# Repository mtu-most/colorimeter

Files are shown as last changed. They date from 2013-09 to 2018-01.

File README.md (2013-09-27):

#Colorimeter and nephalometer firmware

With the files in this directory, you can create a colorimeter and/or
nephalometer, if you have the tools.  You find here:

- colorimeter.ino: c++ source for the firmware, to be uploaded to the arduino.
- \*.scad: models for all the parts which should be produced on a 3-D Printer.  Use OpenSCAD to turn them into STLs.
- colorimeter.sch: Schemetic of the electronics.  Use KiCad to open it.  You are expected to solder everything by hand, so there is no board layout.

To compile the firmware, you need the LcdMenu and DuplexFrequencyCounter libraries from our
[other repository](https://github.com/mtu-most/arduino-libraries).

## Required components
Arduino fio
Adafruit lcd shield PCB
3.3 V lcd unit
3 small PCBs
2 LEDs (860 nm for nephalometry and 620 nm for colorimetry)
3 light to frequency encoders
Some wire to connect it all
Some filament to print the casing
Battery
Some nuts and bolts

## Required tools
3-D printer
FTDI (or equivalent) 3.3 V serial communication cable
Soldering iron

## Steps
1. Load the firmware in the Arduino IDE to flash it into the Arduino (or use make upload).
1. Print all the parts
1. Solder the lcd unit to the lcd shield
1. Cut 3 PCBs to size for the slots
1. Solder the components to the PCBs according to the schematic.  Don't solder anything to the ardiuno; use connectors instead.  Each LED goes on a board with a sensor watching it, the third sensor goes on a board of its own, looking away from the board.
1. Put it all together and close it with screws.

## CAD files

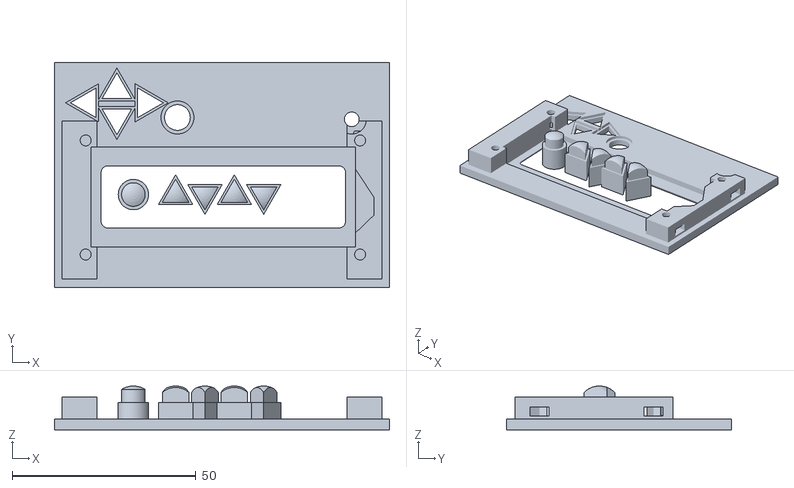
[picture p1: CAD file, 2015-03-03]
stl/adafruit_lcd_shield_face.stl
91.3 x 61.3 x 12.0

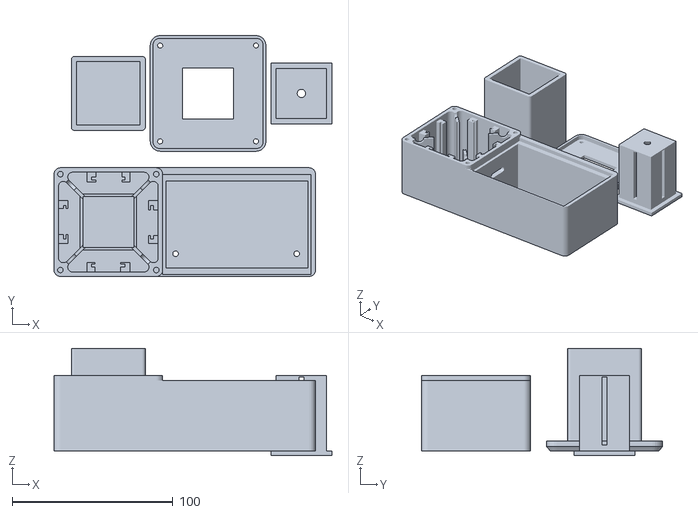
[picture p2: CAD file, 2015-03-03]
stl/Colorimeter_v02.stl
172.8 x 149.8 x 66.6

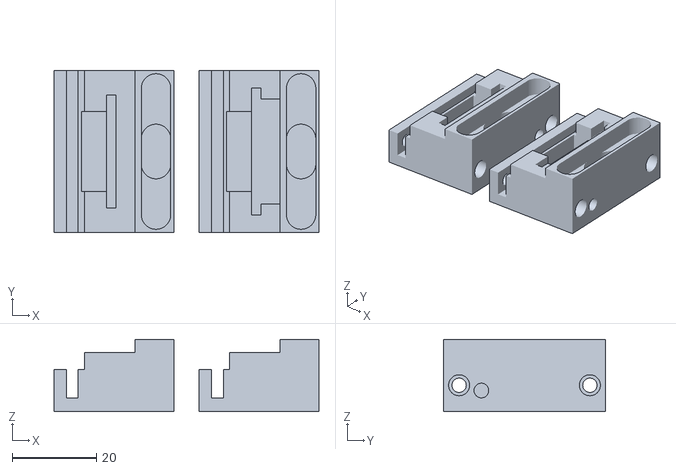
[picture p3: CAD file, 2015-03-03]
stl/board_clips.stl
63.0 x 38.5 x 17.1

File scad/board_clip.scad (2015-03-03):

/**********

 Clips sandwich the various boards together using the holes in the LCD shield and LCD board to
 hold the package together.

 The entire assembled unit will fit inside the colorimeter case and will be held in place by a pair of
 M3 screws through the bottom of the case.

**********/

include <adafruit_lcd_shield_face.scad>
include <fio.scad>
include <fasteners.scad>

// in order to be consistent with fio and adafruit libraries, the clip origin will be the lower left
// as if the LCD shield were sitting atop the clip in it's design orientation

// l || x
// w || y
// t || z

xbee = 0;

// some more fio dims
t_fio_overall = (xbee == 1) ? 16 : 12;  // thickness of Fio with xbee onboard
t_fio_bd_to_xbee = (xbee == 1) ? 8.5 : 4.5; // thickness of fio and xbee w/o battery connector thickness
w_fio_xbee = 25; // width of the xbee socketed
w_fio_sockets = 19; // combined width of battery and USB sockets
clear_w_fio = 1.5;  // additional clearance for fio board
clear_t_fio = 0.75;

t_bd714_overall = 16; // thickness of the populated Adafruit LCD shield
t_lcd_overall = 11.5; // overall thickness of only the LCD board
clear_t_bd714 = 0.75;

l_battery = 63;
w_battery = 37;
t_battery = 7;

clear_comp = 1.5; // clearance between components
clear_lcd = 3; // clearance between lcd and shield

d_holes = 3.4;

// the adafruit LCD board is the longest and widest
l_overall = l_bd714 + 6; // add 3mm to each end
w_overall = w_bd714; // width same as the width of the LCD shield board

// clip dimensions
l_clip = (l_overall - l_battery) / 2 + 5; // battery is shortest - give it 5mm recess
w_clip = w_battery + clear_comp; // battery is the widest component
t_clip = clear_lcd + clear_comp * 2.5 + t_battery + t_fio_overall + t_bd714 + clear_t_bd714;

t_overall = t_clip + t_lcd_overall + lcd_relief;

echo(str("t_clip: ", t_clip, " t_overall: ", t_overall));

// x offsets relative to overall width of assembly; l_overall
x_offset_battery = (l_overall - l_battery) / 2;
x_offset_fio = (l_overall - l_fio) / 2;
x_offset_bd714 = (l_overall - l_bd714) / 2;
x_offset_holes_bd714 = (l_overall - ccl_holes_bd714) / 2;
x_offset_case_screw = x_offset_bd714 + 2;

// y offsets are relative to w_clip
y_offset_battery = t_battery/2 + (w_clip - w_battery) / 2;
y_offset_fio = (w_clip - w_large_fio - clear_w_fio) / 2;
y_offset_bd714 = -1; // there is no y offset for the LCD shield as it's the widest
y_offset_case_screw = 9;

z_offset_battery = (clear_comp + t_battery)/2; // on the bottom
z_offset_fio = clear_comp * 1.5 + t_battery + t_fio_bd_to_xbee; // in middle
z_offset_bd714 = clear_comp * 2.5 + t_battery + t_fio_overall;

module clip(fio_wide_end = 1) {
	difference() {
		// the body of the clip
		cube ([l_clip, w_clip, t_clip]);
		
		// battery opening - bottom most
		translate([x_offset_battery, y_offset_battery, z_offset_battery])
			rotate([0, 90, 0])
				battery();

		if (fio_wide_end == 1) {
			// fio above battery - one end is wider than the other this is wide end w/ sockets
			translate([x_offset_fio, y_offset_fio, z_offset_fio]) {
				cube([l_fio, w_large_fio + clear_w_fio, t_fio + clear_t_fio]); // fio board
		
				translate([0, (w_large_fio + clear_w_fio - w_fio_xbee)/2,  - t_fio_bd_to_xbee])
					cube([l_fio, w_fio_xbee, t_fio_bd_to_xbee]); // xbee opening
		
				translate([-x_offset_fio - 1, (w_large_fio + clear_w_fio - w_fio_sockets)/2, clear_t_fio + t_fio])
					cube([l_fio, w_fio_sockets, 6]); // fio socket opening
			}
	
			// nut trap and hole for attaching to case
			translate([x_offset_case_screw, y_offset_case_screw, 2]) 
				nut_trap();

			// the contrast pot on the shield gets in the way of the one corner:
//			translate([(l_overall - l_bd714) / 2, w_clip-1, t_clip - 5])
//				cube([8, 5, 10]);
		}
		else {
			translate([x_offset_fio, y_offset_fio + (w_large_fio - w_small_fio) / 2, z_offset_fio]) {
				cube([l_fio, w_small_fio + clear_w_fio, t_fio + clear_t_fio]); // fio board

				translate([-x_offset_fio - 1, (w_small_fio + clear_w_fio - w_fio_sockets)/2, clear_t_fio + t_fio])
					cube([l_fio, w_fio_sockets, 6]); // wire recess
			}

			// nut trap and hole for attaching to case
			translate([x_offset_case_screw, w_clip - y_offset_case_screw, 2]) 
				nut_trap();
		}

		// chop some relief for the fio
		translate([x_offset_fio + 3, -1, 1.5 * clear_comp + t_battery])
			cube([l_clip, w_clip + 2, t_clip]);

		// LCD shield board
		translate([x_offset_bd714, y_offset_bd714, z_offset_bd714])
			cube([l_bd714, w_bd714, t_bd714 + clear_t_bd714]);
	
		// clearance is required for sockets and joints on LCD board
		translate([x_offset_bd714 + 7, -1, z_offset_bd714 - clear_comp])
			cube([l_clip, w_clip + 2, 20]);
	
		// holes for screws to affix boards together
		translate([x_offset_holes_bd714, (w_clip - ccw_holes_bd714)/2, -1])
			holes(d_holes, t_clip+2);
	
		// holes for screw caps
		translate([x_offset_holes_bd714, (w_clip - ccw_holes_bd714)/2, -1])
			holes(5, t_clip - 16 + (t_standoff_lcd - h_M25_nut)/2 + t_bd_lcd + 1);	
	
		// recess for cables
		translate([-1, (w_large_fio + clear_w_fio - w_fio_sockets)/2 + y_offset_fio, 5])
			cube([4, w_fio_sockets, w_fio_sockets]);
	}

	// need something to tell the slicer there's a bridge:
		translate([3, 0, 0])
			cube([0.25, w_clip, t_clip]);

}

module battery() {
	hull() {
		cylinder (r=t_battery/2, h=l_battery);

		translate([0, w_battery-t_battery, 0])
			cylinder (r=t_battery / 2, h=l_battery);
	}

	// hole for cables
	translate([0, (w_battery - t_battery) / 2 - 3, -20])
		hull() {
			cylinder (r=t_battery/2, h=l_battery + 40);
	
			translate([0, 6, 0])
				cylinder (r=t_battery / 2, h=l_battery + 40);
		}
}

module holes(diameter, height, fn=48) {
	cylinder(r=diameter/2, h=height, $fn=fn);

	translate([0, ccw_holes_bd714, 0])
		cylinder(r=diameter/2, h=height, $fn=fn);
}

module nut_trap() {
	hull() {
		cylinder(r=d_M3_nut/2, h=h_M3_nut, $fn=6);

		translate([-15, 0, 0])
			cylinder(r=d_M3_nut/2, h=h_M3_nut, $fn=6);
	}

	translate([0, 0, -5])
		cylinder(r=d_M3_screw/2, h=15);
}

module both_clips() {
	rotate([0, 270, 0])
		clip(fio_wide_end = 0);
	
	translate([t_clip+6, 0, 0])
		rotate([0, 270, 0])
			clip(fio_wide_end = 1);
}

// the case interior
module case_interior() {
	// some clearance must be built in
	clear_faceplate = 1;
	clear_interior = 1;
	x_offset_int = (l_face + clear_faceplate - (l_overall + clear_interior)) / 2;
	y_offset_int = (w_face + clear_faceplate - (w_overall + clear_interior)) / 2;
	union() {
		translate([x_offset_int, y_offset_int, 0]) {
			cube([l_overall + clear_interior, w_overall + clear_interior, t_overall + clear_interior]);

		translate([x_offset_case_screw + clear_interior, y_offset_case_screw, -20])
			cylinder(r=d_M3_screw / 2, h = 21);

		translate([l_overall - clear_interior - x_offset_case_screw, y_offset_case_screw, -20])
			cylinder(r=d_M3_screw / 2, h = 21);
		}
		// the faceplate is inset
		translate([0, 0, t_overall - face_thickness + clear_interior])
			cube([l_face + clear_faceplate, w_face + clear_faceplate, face_thickness + 1]); // add 1mm so it clears the top

	}
}

module female_sizeM() {
	union() {
		cylinder(r=4, h=8);

		cylinder(r=5.25, h=2.5);

		translate([0, 0, 5])
			cylinder(r=5.75, h=4, $fn=6);
	}
}

module test_case() {
	difference() {
		translate([2, 2, 0])
		hull() {
			for (i=[0:1]) {
				for (j=[0:1]) {
					translate([i*(l_face + 1), j*(w_face + 1), 0])
						cylinder(r=2, h=t_overall);
				}
			}
		}
	
		translate([2, 2, 2])
			case_interior();

		// power connector
		translate([25, w_overall + 3, 10])
			rotate([270, 0, 0])
				female_sizeM();

		// opening for a cable
		translate([l_overall + 3, w_overall - 17, 4])
			rotate([0, 90, 0])
			rotate([0, 0, 90])
				hull() {
					cylinder(r=0.75, h=5);

					translate([14, 0, 0])
						cylinder(r=0.75, h=5);
			}
	}
}

//test_case();

//both_clips();

//clip(fio_wide_end = 1);

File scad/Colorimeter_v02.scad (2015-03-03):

/**********

This is for the portable version - it shouldn't be played with too much as everything fits with this config!!!

**********/

include <board_clip.scad>

// customizable parameters

// distance from center of cuvette to detector or LED
signal_half_path = 28; // [45:60]

// This sets the number of straight signal paths; 2 paths will generate a square, 3 a hexagon, 4 an octagon...
signal_paths = 2; // [2:4]

// Width of boards sensors and sources are mounted on (mm)
board_width = 20; // [20:30]

// Thickness of boards (mm)
board_thickness = 1.8;

// Board standoff (mm)
board_standoff = 3; // [3:5]

// Cuvette diameter (mm)
cuvette_diameter = 17;

// 1=hemispherical bottom; 0=flat bottom
hemispherical_bottom = 1; // [0:1] 

// Overall length of the cuvette (mm)
cuvette_length = 102; // [30:100]

// Amount of cuvette in analysis area (mm)
analysis_depth = 44.2; // [20:55]

render(5);

module render(render_part) {

	if (render_part == 1)
		case();

	if (render_part == 2)
		rotate([0, 0, 45])
			lid();

	if (render_part == 3)
		translate([0, 0, analysis_depth+t_wall_ext*2])
			mirror([0, 0, 1])
				holder();

	if (render_part == 4)
		cover();

	if (render_part == 5)
		translate([0, 80, 0])
			rotate([0, 0, 45])
				cover();

		case();

		translate([62, 80, 0])
			rotate([0, 0, 45])
				lid();

		translate([120, 80, 0])
			holder();
}

// ignore variable values

// clearances, wall thicknesses, etc.
pad_board = 3;
clear_board = 0.4;
clear_cuvette = 0.4;
clear_faceplate = 4;
t_wall_ext = 2.8; // exterior wall thickness
t_wall_int = 2.1; // interior wall thickness
r_apex_ext = 4; // radius of exterior corners
r_apex_int = 3; // radius of interior corners
overlap_lid = 3.5;
flange_holder = 5;

// segment dimensions representing exterior of case
// everything is calculated in terms of circular segments from which trapezoids are constructed
a_seg = 360/signal_paths/2; // angle of segment arc
tan_h_a_seg = tan(a_seg/2);
cos_h_a_seg = cos(a_seg/2);
sin_h_a_seg = sin(a_seg/2);
h_ext = signal_half_path+t_wall_ext+board_standoff; // height of the triangle making up the segment
r_ext = h_ext/cos_h_a_seg; // radius of the segment; distance from center to corner
t_ext = analysis_depth+t_wall_ext; // thickness of the segment

echo(str("2*h_ext = ", 2 * h_ext));
echo(str("t_ext =", t_ext));

// cuvette holder dimensions -- like the case, it is based on a segment
h_holder = 25.4/2+2.8; // this is the height of triangle making up the holder, must be big enough for the largest cuvette and have allowance for wall thickness
r_holder = h_holder/cos_h_a_seg;
clear_holder = 0.5;

// radii of rounded apex centers
r_c_apex_ext = r_ext-r_apex_ext/cos_h_a_seg;
r1_c_apex_int = r_ext-(r_apex_int+t_wall_ext)/cos_h_a_seg;
r2_c_apex_int = r_holder+r_apex_int/cos_h_a_seg;

// cavities are trapezoids with rounded apexes:
b1 = r1_c_apex_int*sin_h_a_seg*2-(2*r_apex_int+t_wall_int)/cos_h_a_seg;
b2 = r2_c_apex_int*sin_h_a_seg*2-(2*r_apex_int+t_wall_int)/cos_h_a_seg;
h = (r1_c_apex_int-r2_c_apex_int)*cos_h_a_seg;

d_M3_screw = 3.5; // measured 2.9
d_M3_screw_head = 5.8; // measured 5.5
d_M3_washer = 6.9; // measured 6.7
d_M3_nut = 6.2;
h_M3_nut = 2.7; // measured 2.35
d_M3_cap = 5.5;
h_M3_cap = 3;

d_M4_screw = 4.3;
d_M4_cap = 7.4; // measured 12
h_M4_cap = 4;
d_M4_nut = 8.7;
h_M4_nut = 3.5; // measured 3.1
h_M4_locknut = 5;
d_M4_washer = 9; // measured 8.75
h_M4_washer = 0.75;

d_M6_screw = 6.5;
d_M6_nut = 11.3;
h_M6_nut = 4.2;

d_M8_screw = 8.4;
d_M8_nut = 15;
h_M8_nut = 6.35;
d_M8_washer= 16;
h_M8_washer = 1.5;

module exterior_sensor(height) {
	union() {
		hull() {
			for (i=[0:signal_paths*2-1]) 
				rotate([0, 0, a_seg*i])
					translate([0, r_c_apex_ext, 0])
						cylinder(r=r_apex_ext, h=height, $fn=24);
		}

	}
}

module exterior_interface(height) {
	hull() {
		translate([-h_ext+r_apex_ext, -l_face/2-r_apex_ext, 0])
			cylinder(r=r_apex_ext, h=height, $fn=24);

		translate([h_ext-r_apex_ext, -l_face/2-r_apex_ext, 0])
			cylinder(r=r_apex_ext, h=height, $fn=24);

		translate([h_ext-r_apex_ext, l_face/2+r_apex_ext, 0])
			cylinder(r=r_apex_ext, h=height, $fn=24);

		translate([-h_ext+r_apex_ext, l_face/2+r_apex_ext, 0])
			cylinder(r=r_apex_ext, h=height, $fn=24);
	}
}

module cavity() {
	x_retainer = board_width+2*(clear_board+pad_board);
	y_retainer = 2*board_standoff;

	translate([0, -h/2-r_apex_int, 0])
	difference() {
		union() {
			// trapezoid with rounded apexes:
			hull() {
				translate([-b1/2, -h/2, 0])
					cylinder(r=r_apex_int, h=t_ext);
		
				translate([b1/2, -h/2, 0])
					cylinder(r=r_apex_int, h=t_ext);
		
				translate([b2/2, h/2, 0])
					cylinder(r=r_apex_int, h=t_ext);
		
				translate([-b2/2, h/2, 0])
					cylinder(r=r_apex_int, h=t_ext);
			}
	
			// wire race
			translate([-b1/2+r_apex_int*sin_h_a_seg, -h/2+r_apex_int*cos_h_a_seg, t_ext-t_wall_ext])
				rotate([0, -90, -a_seg/2])
					cylinder(r=3.5, h=t_wall_int+r_apex_int+1);
		}
	
		// sensor/LED board retainers
		translate([-x_retainer/2, -h/2-r_apex_int, -1])
			difference() {
				cube([x_retainer, y_retainer, t_ext-4]);

				translate([pad_board, board_standoff, -1])
					cube([x_retainer-2*pad_board, board_thickness, t_ext-2]);

				translate([pad_board+2, 0, -1])
					cube([board_width-4, y_retainer+1, t_ext-2]);
			}

		// lip at bottom of cuvette holder
		translate([-b2*2, h/2+1, -1])
			cube([b2*4, 3, 2.5]);

	}
}

module case(
	portable = 1) {

	difference() {
		union() {
			rotate([0, 0, a_seg/2])
				exterior_sensor(t_ext);

			if (portable == 1)
				hull() {
					translate([h_ext + 91, h_ext - r_apex_ext, 0])
						cylinder(r=r_apex_ext, h=t_ext-3, $fn=24);
	
					translate([h_ext + 91, -h_ext + r_apex_ext, 0])
						cylinder(r=r_apex_ext, h=t_ext-3, $fn=24);

					translate([h_ext - r_apex_ext, h_ext - r_apex_ext, 0])
						cylinder(r=r_apex_ext, h=t_ext-3, $fn=24);
	
					translate([h_ext - r_apex_ext, -h_ext + r_apex_ext, 0])
						cylinder(r=r_apex_ext, h=t_ext-3, $fn=24);
				}
		}

		// cavities
		for (i=[0:signal_paths*2-1])
			rotate([0, 0, a_seg*i])
				translate([0, -h_holder, t_wall_ext])
					cavity();

		rotate([0, 0, a_seg/2]) {
			translate([0, 0, t_ext-16+t_wall_ext])
				holes(d_M3_screw/2, 16-t_wall_ext+1, 24);
	
			translate([0, 0, -1])
				holes((d_M3_nut+1)/2, t_ext-16+t_wall_ext-0.25+1, 6);
		}
	
		// cuvette holder
		translate([0, 0, t_wall_ext])
			rotate([0, 0, (1-signal_paths%2)*a_seg/2])
				cylinder(r=r_holder+clear_holder, h=t_ext, $fn=signal_paths*2);

		if (portable == 1) {
			// interior of electronics case
			translate([h_ext, -(w_face + clear_faceplate)/2, 2])
				case_interior();

			// power connector
			translate([h_ext + (l_overall + 2 * t_wall_ext)/2 - 10, h_ext - r_apex_ext - 2.5, 10])
				rotate([270, 0, 0])
					rotate([0, 0, 30])
						female_sizeM();

			// switch
//			translate([h_ext + (l_overall + 2 * t_wall_ext)/2 + 10,  h_ext - r_apex_ext - 0.5, 10])
//				rotate([270, 0, 0])
//					switch();
		}

		// wire entry
		rotate([0, 0, -90])
		translate([0, h_ext-t_wall_ext-1, t_ext - 20])
			rotate([-90, 0, 0])
				hull() {
					translate([-board_width/2 + 4, 0, 0])
						cylinder(r=2, h=t_wall_ext+5);

					translate([board_width/2 - 4, 0, 0])
						cylinder(r=2, h=t_wall_ext+5);
				}
	}

/*
	// following to check wall thicknesses are correct
	translate([0, h_ext-t_wall_ext/2, 0])
		#cylinder(r=t_wall_ext/2, h=100, $fn=48);
	
	rotate([0, 0, a_seg/2])
	translate([0, r_holder, 0])
		#cylinder(r=t_wall_int/2, h=100, $fn=48);
*/
}

module holes(radius, height, fn) {
	for (i=[0:signal_paths*2-1]) {
		rotate([0, 0, a_seg*i])
			translate([0, -r_c_apex_ext, 0])
				cylinder(r=radius, h=height, $fn=fn);
	}
}

module holder() {
	rotate([0, 0, a_seg/2])
		difference() {
			union() {
				// body
				cylinder(r=r_holder+clear_cuvette/2, h=analysis_depth+t_wall_ext, $fn=signal_paths*2);
	
				// flange
				translate([0, 0, analysis_depth+t_wall_ext])
					cylinder(r=r_holder+flange_holder, h=t_wall_ext, $fn=signal_paths*2);
			}

			if (hemispherical_bottom == 0) {
				cylinder(r=cuvette_diameter/2+clear_cuvette/2, h=analysis_depth+2*t_wall_ext+1);
			}
			else {
				translate([0, 0, cuvette_diameter/2])
					union() {
						sphere(r=cuvette_diameter/2+clear_cuvette);

						cylinder(r=cuvette_diameter/2+clear_cuvette, h=analysis_depth+2*t_wall_ext+1);
					}
			}

			for(i=[0:signal_paths-1]) {
				rotate([0, 0, a_seg*i+a_seg/2])
				translate([-1.5, -(r_holder*2+2)/2, 1])
					cube([3, r_holder*2+2, analysis_depth-2]);
			}
		}
}
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

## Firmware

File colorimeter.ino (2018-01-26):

// vim: set foldmethod=marker filetype=cpp:

// Pin layout of the colorimeter:  {{{
// D10	Enable for main sensor (should always be on). (yellow)
#define SENSOR_MAIN 10
// D11	Power for sensors (should always be high). (brown)
//	Power for LEDs (should always be high). (red)
#define POWER 11
// D2	Enable for orange sensor. (purple)
#define SENSOR_620 2
// D3	Enable for IR sensor. (green)
#define SENSOR_IR 3

// D9	Enable for orange LED. (grey)
#define LED_620 9
// D8	Enable for IR LED. (blue)
#define LED_IR 8

// D4	Count from main sensor. (black)
#define COUNT_MAIN 4
// D5	Count from reference sensors (only one must be enabled). (orange)
#define COUNT_REF 5

// A4 + A5: I2C pins; LCD shield connected to it.

// Enable pins are active by setting them to output low; inactive by setting
// them to input.  So all are set to low and toggling is done by changing
// the pin direction.
// }}}

enum SourceNames {	// {{{
	SOURCE_NONE,
	SOURCE_IR,
	SOURCE_620
}; // }}}

// Includes. {{{
#define SERIAL_LCD	// Output lcd display on serial port.

#include <EEPROM.h>
#include <Wire.h>
#include <Adafruit_RGBLCDShield.h>
#include <LcdMenu.h>
#include <DuplexFrequencyCounter.h>
// }}}

// Globals.  {{{
#define WARMUP_TIME 1000	// For testing, 1 second warmup time will do.
static uint16_t measure_time = 1000;
Adafruit_RGBLCDShield lcd;
static uint32_t newsource = 0;
static uint32_t cNTU = 4000;	// centi-nephalometric turbidity units.
static float cod_zero_value = ~0;
static uint32_t sensor, ref;	// Make these global for debugging.

// Nephalometry calibration values.
struct Neph_cal {	// {{{
	int num;
	float x;
	float y;
	float xy;
	float x2;
	float y2;
	float a;
	float b;
};	// }}}

// The thing below is in eeprom, so the bytes must be directly addressable.
typedef struct
{
	float cod;
	Neph_cal neph;
} cal_t;
static union {
	cal_t c;
	char bytes[sizeof(cal_t)];
} cal;
// }}}

void writeCal()	// {{{
{
	for (uint8_t i = 0; i < sizeof(cal); ++i)
		EEPROM.write(i, cal.bytes[i]);
}	// }}}

void setSource(uint8_t source)	// {{{
{
	pinMode(SENSOR_IR, INPUT);
	pinMode(SENSOR_620, INPUT);
	pinMode(LED_IR, INPUT);
	pinMode(LED_620, INPUT);

	switch (source)
	{
	case SOURCE_NONE:
		break;
	case SOURCE_IR:
		pinMode(SENSOR_IR, OUTPUT);
		pinMode(LED_IR, OUTPUT);
		break;
	case SOURCE_620:
		pinMode(SENSOR_620, OUTPUT);
		pinMode(LED_620, OUTPUT);
		break;
	}
	newsource = millis();
}	// }}}

void waitForSource()	// {{{
{
	uint32_t wait = millis() - newsource;
	if (wait < WARMUP_TIME)
	{
		lcd.clear();
		message("Source warms up", "Please wait");
		delay(WARMUP_TIME - wait);
	}
}	// }}}

float getSensor()	// {{{
{
	readFreq(measure_time, sensor, ref);
	return (float)sensor / ref;
}	// }}}

uint8_t checkButton(bool block) { // {{{
	while (true) {
		uint8_t ret = lcd.readButtons();
		if (ret != BUTTON_NONE || !block)
			return ret;
	}
} // }}}

// Menus, including implementation of the functions.  {{{
MenuItem(COD_zero)	// {{{
{
	waitForSource();
	cod_zero_value = getSensor();
	return 1;
}	// }}}

MenuItem(COD_measure)	// {{{
{
	static uint32_t index = 0;
	// Don't measure without zero.
	if (cod_zero_value == ~0)
	{
		message("Please zero the", "instrument first");
		checkButton(true);
		return -1;
	}
	waitForSource();
	message("Measuring");
	float data = getSensor();
	// TODO: compute concentration.
	float trans = data / cod_zero_value;
	float absorb = -log10(trans);
	lcd.clear();
	lcd.print("T:");
	lcd.print(trans, 3);
	lcd.setCursor(8, 0);
	lcd.print("A:");
	lcd.print(absorb, 3);
	lcd.setCursor(0, 1);
	lcd.print(index);
	lcd.print(" ");
	unsigned long m = millis();
	lcd.print(m);
	Serial.print(absorb, 3);
	Serial.print("\t");
	Serial.print(index++);
	Serial.print("\t");
	Serial.print(m);
	Serial.print("\n");
	checkButton(true);
	return 0;
}	// }}}

MenuItem(COD_calibrate)	// {{{
{
	waitForSource();
	return -1;
}	// }}}

Menu <3> COD_Menu("COD", (char const *[]){"Zero", "Measure", "Calibrate"}, (action *[]){&COD_zero, &COD_measure, &COD_calibrate});

MenuItem(doCOD)	// {{{
{
	setSource(SOURCE_620);
	bool ret = COD_Menu.run(true);
	setSource(SOURCE_NONE);
	return ret;
}	// }}}

MenuItem(Neph_measure)	// {{{
{
	static uint32_t index = 0;
	waitForSource();
	message("Measuring");
	float data = getSensor();
	if (isnan(cal.c.neph.a))
	{
		lcd.clear();
		lcd.print("Not calibrated");
		lcd.setCursor(0, 1);
		lcd.print("Read: ");
		int power = 0;
		while (data < 1) {
			power -= 1;
			data *= 10;
		}
		while (data >= 10) {
			power += 1;
			data /= 10;
		}
		lcd.print(data);
		lcd.print("e");
		lcd.print(power);
	}
	else
	{
		float turb = cal.c.neph.a * data + cal.c.neph.b;
		lcd.clear();
		lcd.print(turb, 3);
		lcd.print(" NTU");
		lcd.setCursor(0, 1);
		lcd.print("index: ");
		lcd.print(index);
		Serial.print(index++);
		Serial.print("\t");
		Serial.print(turb);
		Serial.print("\t");
		Serial.print(millis());
		Serial.print("\n");
	}
	checkButton(true);
	return 0;
}	// }}}

MenuItem(Neph_recalibrate)	// {{{
{
	cal.c.neph.a = NAN;
	cal.c.neph.b = NAN;
	cal.c.neph.num = 0;
	cal.c.neph.x = 0;
	cal.c.neph.y = 0;
	cal.c.neph.xy = 0;
	cal.c.neph.x2 = 0;
	cal.c.neph.y2 = 0;
	writeCal();
	message("Calibration", "erased.");
	checkButton(true);
	return 1;
}	// }}}

MenuItem(Neph_calibrate)	// {{{
{
	message("Calibration:", "0000.00 NTU     ");
	cNTU = readNum(0, 1, 4, 2, cNTU);
	waitForSource();
	message("Calibrating");
	float data = getSensor();
	cal.c.neph.x += data;
	cal.c.neph.y += cNTU / 100.;
	cal.c.neph.xy += data * (cNTU / 100.);
	cal.c.neph.x2 += data * data;
	cal.c.neph.y2 += (cNTU / 100.) * (cNTU / 100.);
	++cal.c.neph.num;
	if (cal.c.neph.num >= 4 && cal.c.neph.y2 != cal.c.neph.y * cal.c.neph.y)
	{
		cal.c.neph.a = (cal.c.neph.xy - cal.c.neph.x * cal.c.neph.y / cal.c.neph.num) / (cal.c.neph.x2 - cal.c.neph.x * cal.c.neph.x / cal.c.neph.num);
		cal.c.neph.b = (cal.c.neph.y - cal.c.neph.a * cal.c.neph.x) / cal.c.neph.num;
		writeCal();
		message("Calibration read");
		lcd.setCursor(0, 1);
		lcd.print("Error: ");
		lcd.print((cal.c.neph.y2 + cal.c.neph.a * cal.c.neph.a * cal.c.neph.x2 - 2 * cal.c.neph.a * cal.c.neph.xy - 2 * cal.c.neph.b * cal.c.neph.y + 2 * cal.c.neph.a * cal.c.neph.b + cal.c.neph.x) / cal.c.neph.num + cal.c.neph.b * cal.c.neph.b);
	}
	else
		message("Calibration read", "More needed");
	checkButton(true);
	return 0;
}	// }}}

Menu <3> Neph_Menu("Nephalometry", (char const *[]){"Measure", "Recalibrate", "Calibrate"}, (action *[]){&Neph_measure, &Neph_recalibrate, &Neph_calibrate});

MenuItem(doNeph)	// {{{
{
	setSource(SOURCE_IR);
	bool ret = Neph_Menu.run(true);
	setSource(SOURCE_NONE);
	return ret;
}	// }}}

void debug_newsource(uint8_t s) // {{{
{
	setSource(s);
	lcd.setCursor(0, 1);
	lcd.print("Source: ");
	switch (s)
	{
	case SOURCE_NONE:
		lcd.print("None ");
		break;
	case SOURCE_620:
		lcd.print("620  ");
		break;
	case SOURCE_IR:
		lcd.print("IR");
		break;
	}
}	// }}}

MenuItem(debug)	// {{{
{
	measure_time = 100;
	lcd.print("Time: 0100 ms");
	uint8_t s = SOURCE_NONE;
	while (lcd.readButtons() != 0) {}
	debug_newsource(s);
	while (true)
	{
		uint8_t b = lcd.readButtons();
		switch (b)
		{
		case 0:
			break;
		case BUTTON_UP:
			s = (s + 1) % 3;
			debug_newsource(s);
			while (lcd.readButtons() != 0) {}
			break;
		case BUTTON_DOWN:
			s = (s - 1 + 3) % 3;
			debug_newsource(s);;
			while (lcd.readButtons() != 0) {}
			break;
		case BUTTON_LEFT:
			setSource(SOURCE_NONE);
			return 0;
		case BUTTON_RIGHT:
		case BUTTON_SELECT:
			measure_time = readNum(6, 0, 4, 0, measure_time);
			while (lcd.readButtons() != 0) {}
		}
		// Let the serial port catch up.
		while (~UCSR0A & (1 << 5)) {}
		// Send data to the port.
		unsigned long m = millis();
		float data = getSensor();
		Serial.print(m);
		Serial.print("\t");
		Serial.print(data * 1e6);
		Serial.print("\t");
		Serial.print(sensor);
		Serial.print("\t");
		Serial.print(ref);
		Serial.print("\t");
		Serial.print(s);
		Serial.print("\t");
		Serial.print(measure_time);
		Serial.print("\n");
	}
}	// }}}

Menu <3> MainMenu("Main menu", (char const *[]){"COD", "Nephalometry", "Debug"}, (action *[]){&doCOD, &doNeph, &debug});
// }}}

// Arduino main functions. {{{
void setup() {	// {{{
	Serial.begin(9600);
	lcd.begin(16, 2);
	pinMode(SENSOR_MAIN, OUTPUT);
	pinMode(POWER, OUTPUT);
	digitalWrite(SENSOR_MAIN, LOW);
	digitalWrite(POWER, HIGH);
	digitalWrite(SENSOR_620, LOW);
	digitalWrite(SENSOR_IR, LOW);
	digitalWrite(LED_620, LOW);
	digitalWrite(LED_IR, LOW);
	setSource(SOURCE_NONE);
	for (uint8_t i = 0; i < sizeof(cal); ++i)
		cal.bytes[i] = EEPROM.read(i);
}	// }}}

void loop() {	// {{{
	MainMenu.run(true);
}	// }}}
// }}}

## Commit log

2013-09-11 fixed calibration.
2015-03-03 added stls and scads
    [Colorimeter_v02.scad, Colorimeter_v02.stl, adafruit_lcd_shield_face.stl, board_clip.scad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]
